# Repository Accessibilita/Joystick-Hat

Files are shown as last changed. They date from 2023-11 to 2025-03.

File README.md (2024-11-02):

# Joystick-HID (0.2a)
A custom open source PCB for controlling an open source wheel chair! This PCB contains all the necessary electronics for interfacing and powering all the components/peripherals that will be used to build a wheel chair human machine interface consisting of this PCB, analog JoyStick module, buttons, rotary switches, and 3D printed housing. JoyStick-HID is just one of the many PCBs being developed for our open source wheel chair electrical system we are developing with the Accessibilita project for the Mobility Independence Foundation (themif.org) !!

Functional Block Diagram of Board 

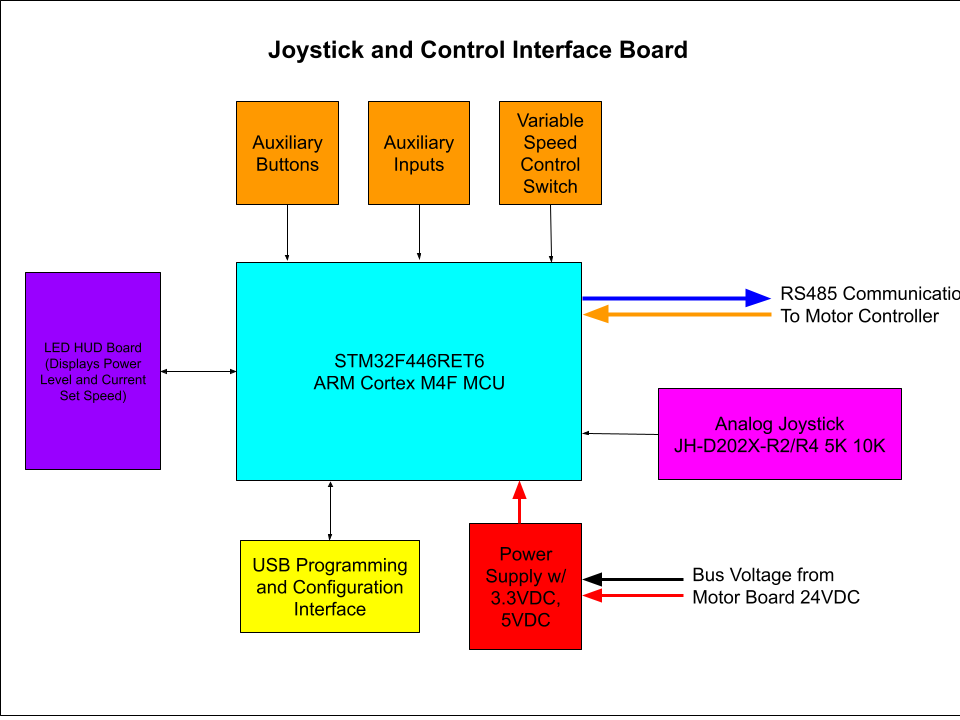
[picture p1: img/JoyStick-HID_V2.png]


Quick Specs of the Hat:
- STM32F446RET6 100TQFP ARM Cortex M4 Microcontoller
- ARM Cortex M Serial Debu Interface/connector for in system programming and development 
- MAX3535ECWI+T RS485 Transceiver for communicating with main motor controller
- D24V22F5 2.5A 5VDC Voltage Regulator Module
- D24V22F3 2.5A 3.3VDC Voltage Regulator Module
- 24V Power Input with High Current Pheonix Contact Connector
- 8 Debug LEDs for STM32F446RET6
- Onboard Battery for STM32F446RET6 RealTime Clock
- Interface for JoyStick, JH-D202X-R2/R4 Joystick 5K https://protosupplies.com/product/jh-d202x-r2-r4-joystick-5k/
- Interface for two Rotary Switches
- Interface for 8 Momentary swiches/buttons
- Interface for LED driver board, this additional board drives LEDs in the arm wrest indicating battery level and current set speed
- STM32 will run FreeRTOS w/ Custom Processes written for all functionality with priority scheduling for safety rated functions.

This hat is intended as a developmental platform that can function in the field, it has all the features needed to control the wheel chair with additional feature that will make software development easier. The final version will be much simpler and low cost, this is only the beginning. 

2D Render of JoyStick-HID Hat in KiCAD 8.0
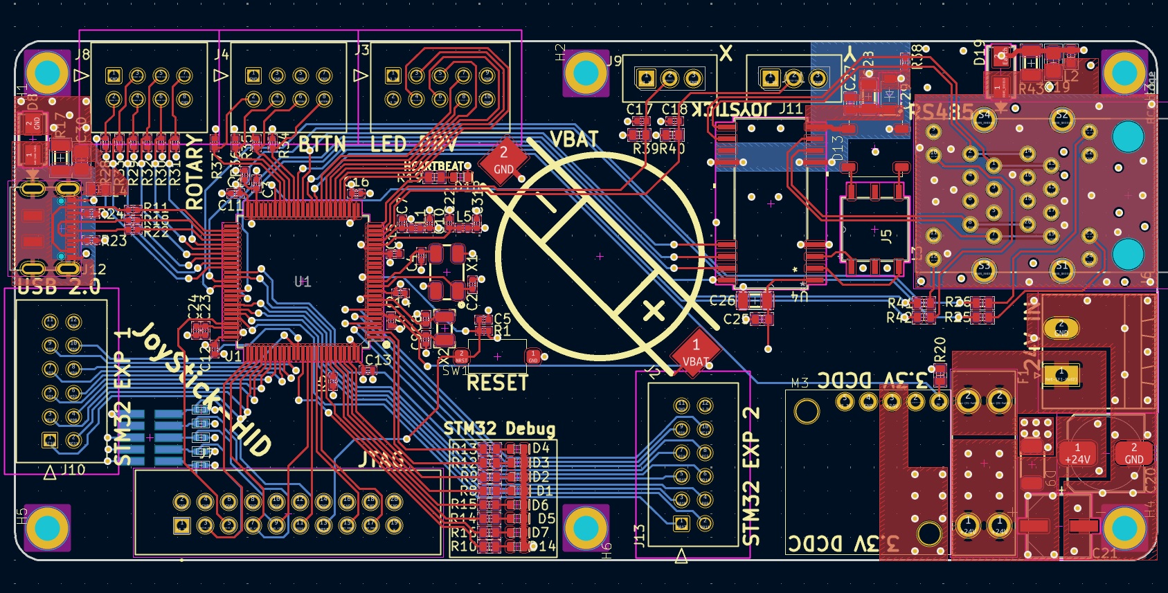
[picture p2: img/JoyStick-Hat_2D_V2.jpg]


3D Renders of JoyStick-HID Hat in KiCAD 8.0 3D Viewer 

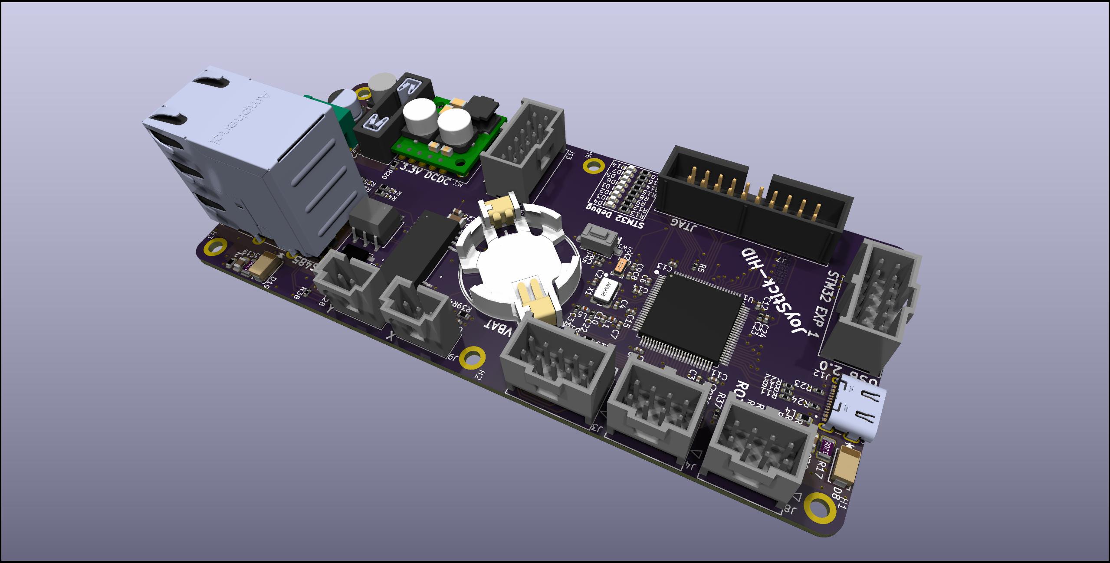
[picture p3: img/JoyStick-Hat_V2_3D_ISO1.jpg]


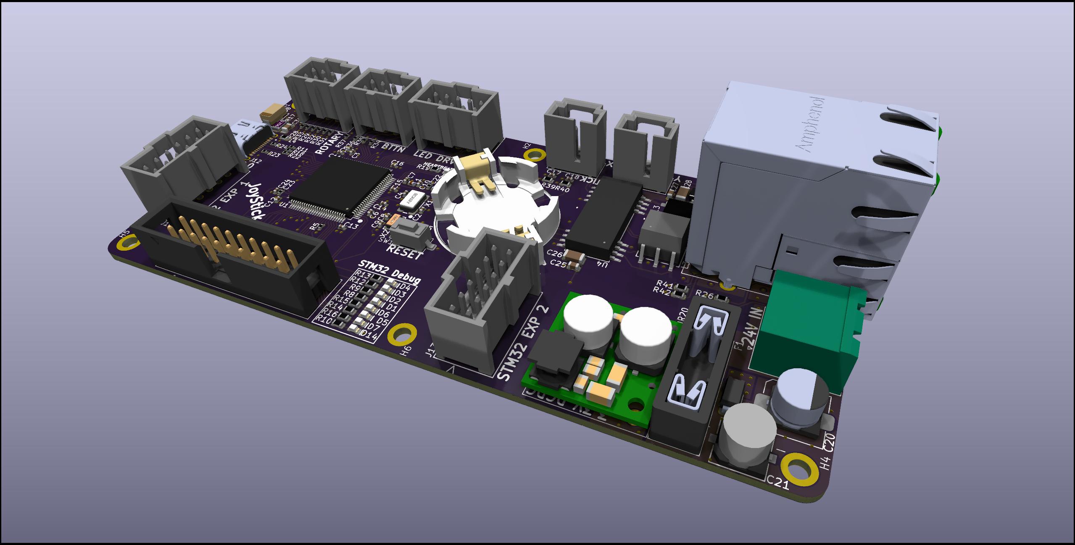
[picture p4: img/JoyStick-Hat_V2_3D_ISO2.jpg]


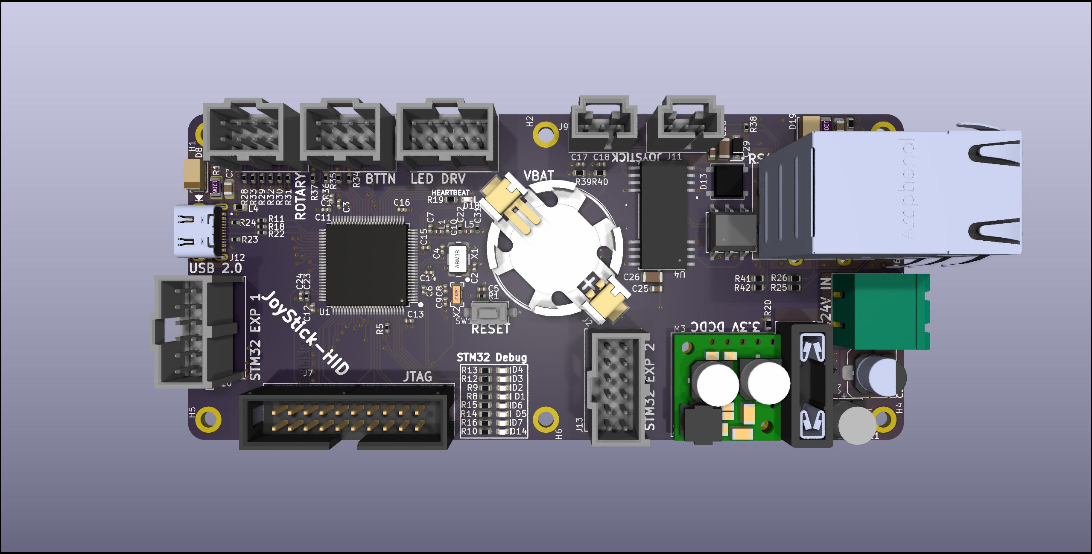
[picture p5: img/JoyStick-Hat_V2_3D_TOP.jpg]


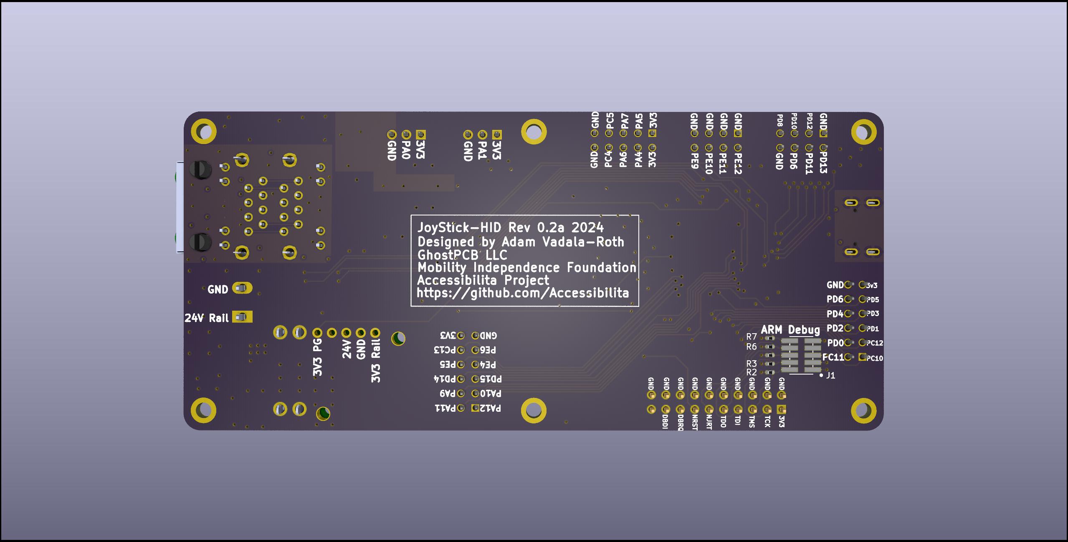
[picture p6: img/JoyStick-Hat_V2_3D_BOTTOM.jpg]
3D_Render_Bottom


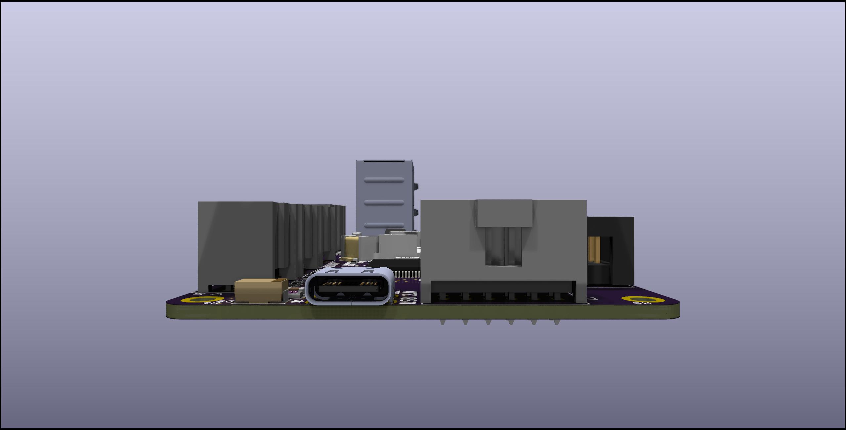
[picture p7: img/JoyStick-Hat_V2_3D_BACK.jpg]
3D_Render_Back


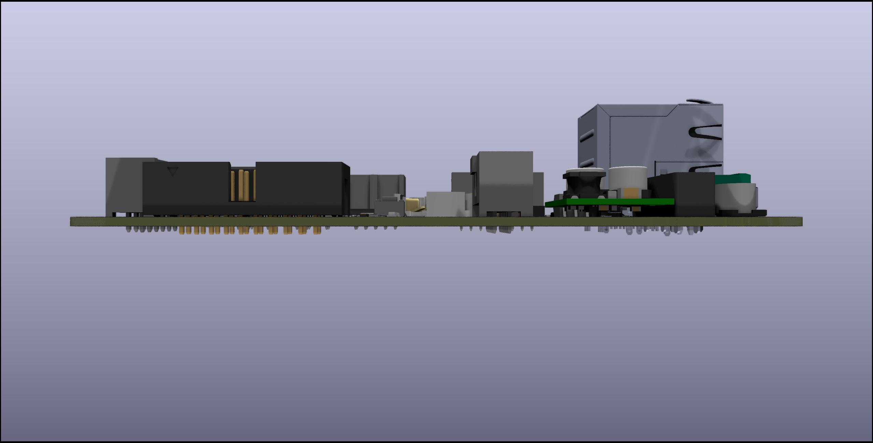
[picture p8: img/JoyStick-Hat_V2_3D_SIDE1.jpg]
3D_Render_SIDE1


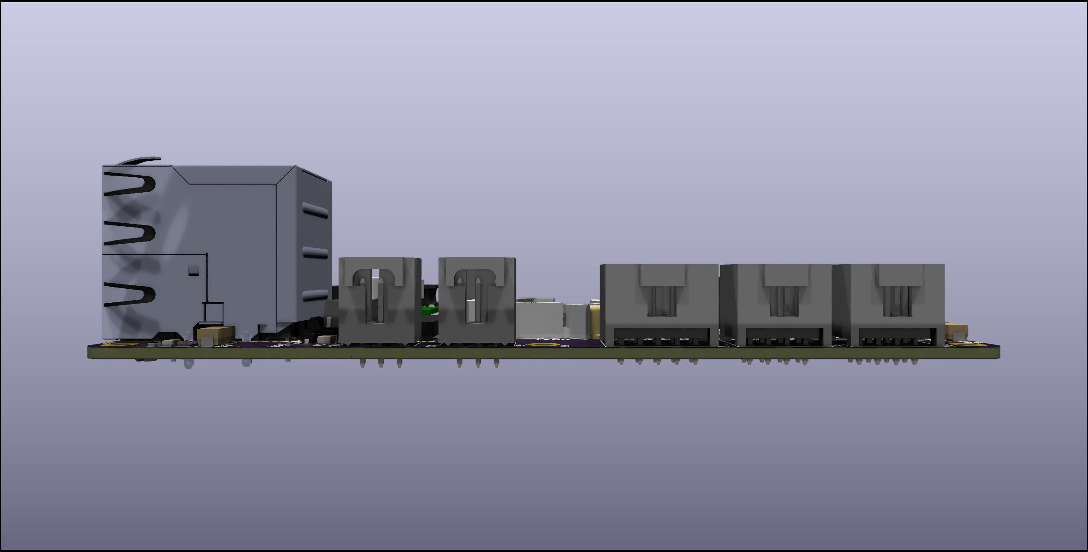
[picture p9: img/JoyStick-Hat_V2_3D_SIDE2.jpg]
3D_Render_SIDE2


# Joystick-Hat (0.1a)
Version 0.1a JoyStick HID:

RPi Hat for controlling an open source wheel chair! This hat contains all the necessary electronics for interfacing and powering all the components/peripherals that will be used to control the open source wheel chair electrical system we are developing with the Accessibilita project !!

Functional Block Diagram of Board 

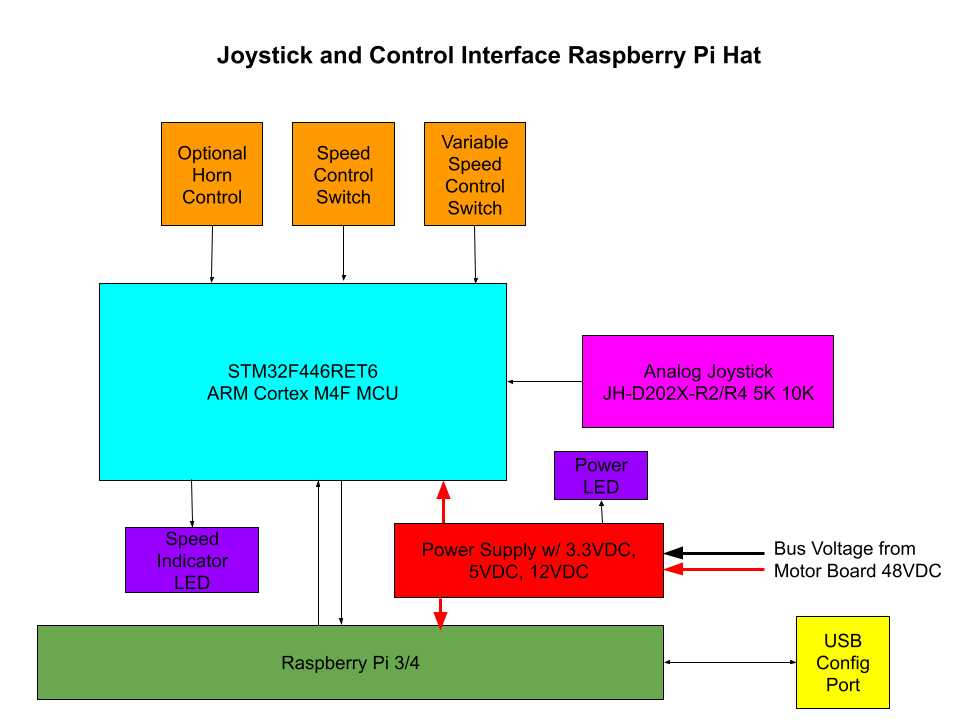
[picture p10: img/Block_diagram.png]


Quick Specs of the Hat:
- STM32F446RET6 100TQFP ARM Cortex M4 Microcontoller
- ARM Cortex M Serial Debu Interface/connector for in system programming and development 
- MAX3535ECWI+T RS485 Transceiver for communicating with main motor controller
- D24V22F5 2.5A 5VDC Voltage Regulator Module
- D24V22F3 2.5A 3.3VDC Voltage Regulator Module
- D24V22F12 2.5A 12VDC Voltage Regulator Module
- 24V Power Input with High Current Pheonix Contact Connector
- 12V Power output with High current Phoenix Contact Connector
- Rapsberry Pi 5 Running ROS2, directly power via header from 5VDC rail
- 8 Debug LEDs for STM32F446RET6
- 8 Debug LEDs for RPi 5
- Onboard Battery for STM32F446RET6 RealTime Clock
- Interface for JoyStick, JH-D202X-R2/R4 Joystick 5K https://protosupplies.com/product/jh-d202x-r2-r4-joystick-5k/
- Interface for two Rotary Switches
- Interface for 8 Momentary swiches/buttons
- Interface for LED driver board, this additional board drives LEDs in the arm wrest indicating battery level and current set speed
- STM32 will run custom FreeRTOS or ROS-Micro more to follow

This hat is intended as a developmental platform that can function in the field, it has all the features needed to control the wheel chair with additional feature that will make software development easier. The final version will be much simpler and low cost, this is only the beginning. 

2D Render of JoyStick-HID Hat in KiCAD 8.0
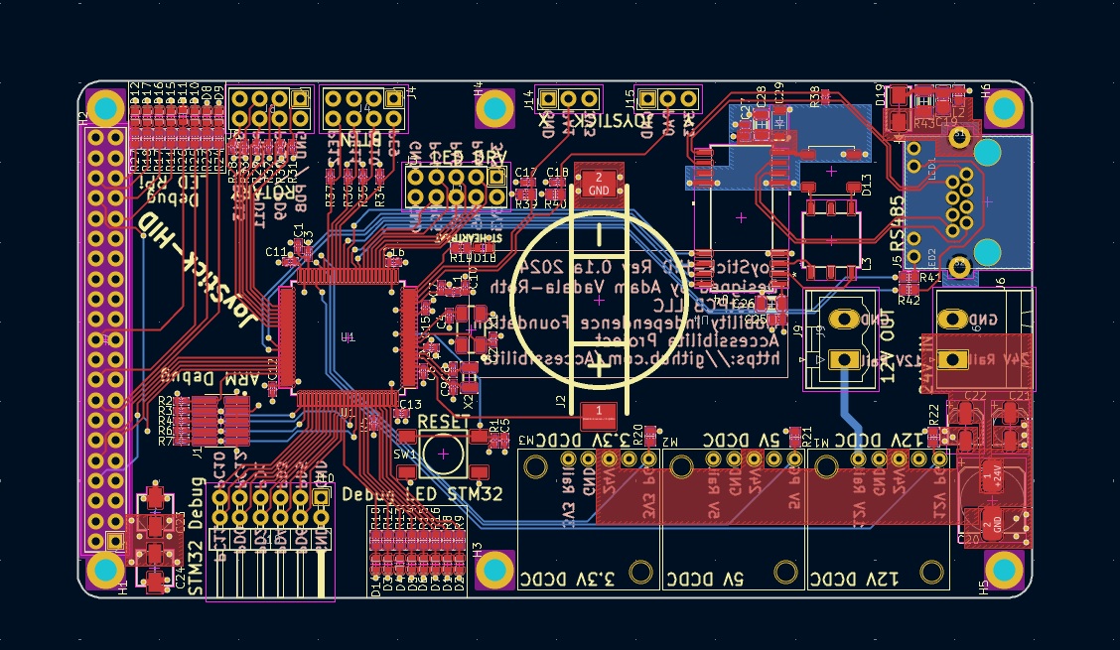
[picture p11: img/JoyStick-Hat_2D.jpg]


3D Renders of JoyStick-HID Hat in KiCAD 8.0 3D Viewer 

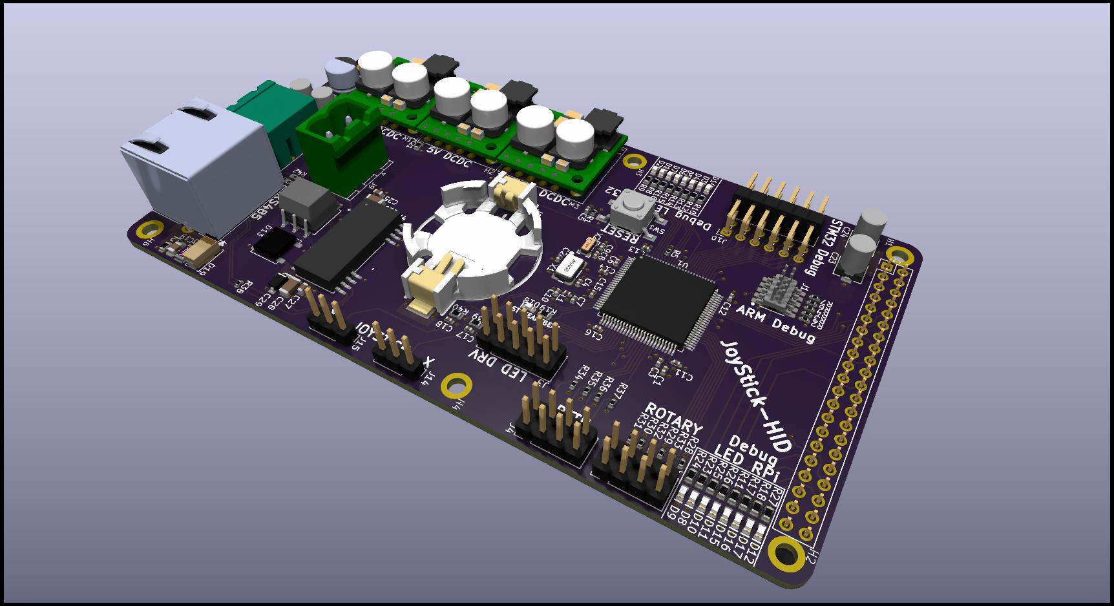
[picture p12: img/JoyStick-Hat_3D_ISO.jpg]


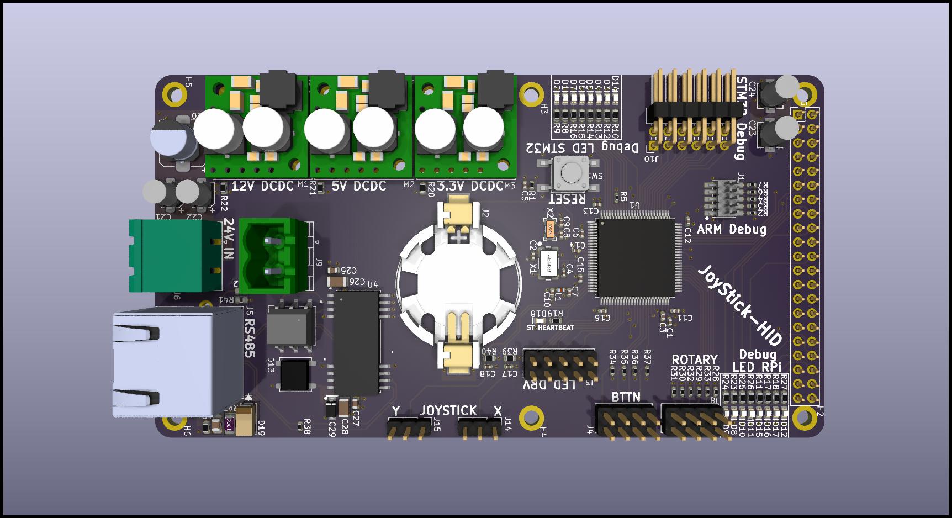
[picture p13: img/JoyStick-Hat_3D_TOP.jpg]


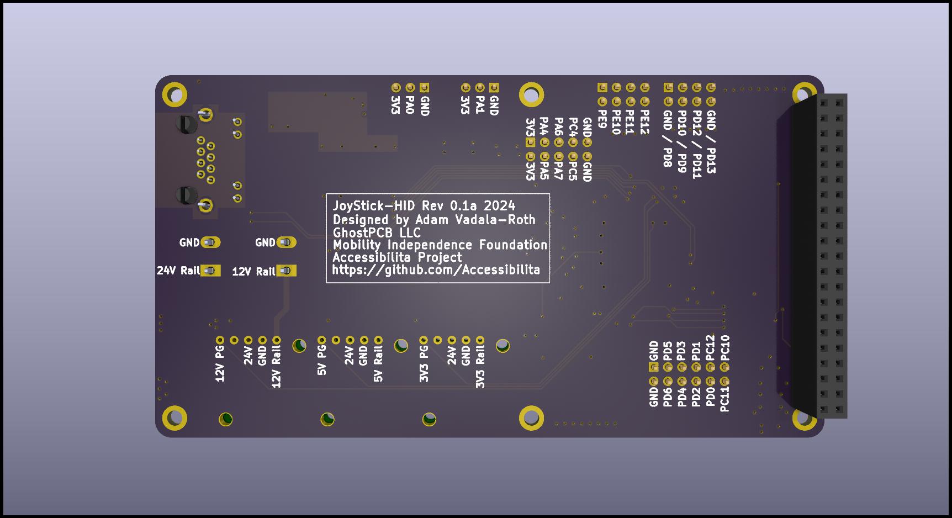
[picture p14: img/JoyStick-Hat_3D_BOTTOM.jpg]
3D_Render_Bottom


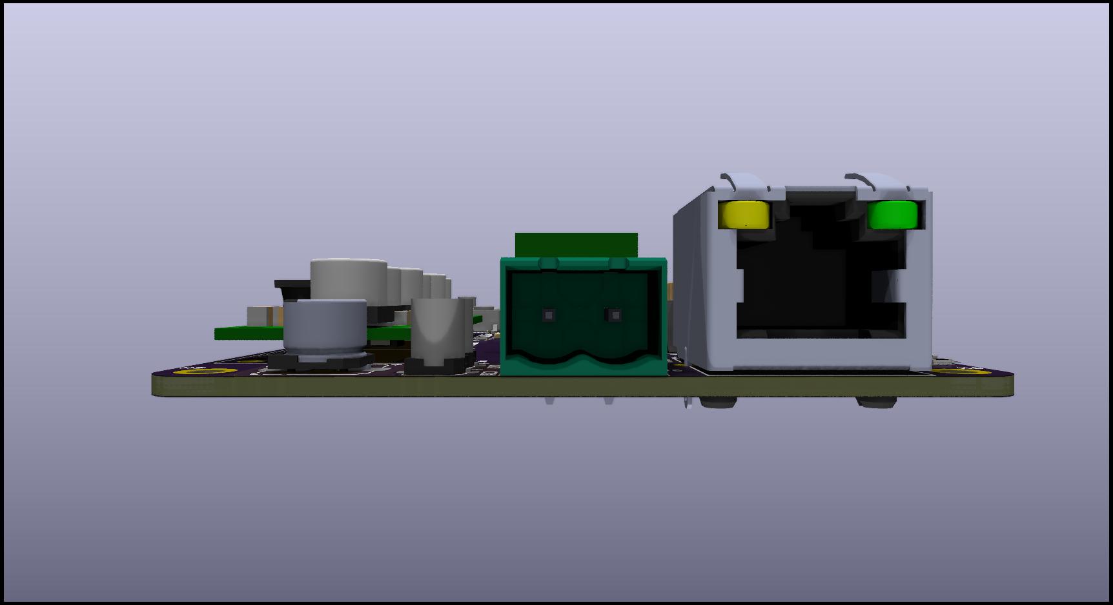
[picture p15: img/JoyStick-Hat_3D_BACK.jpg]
3D_Render_Back


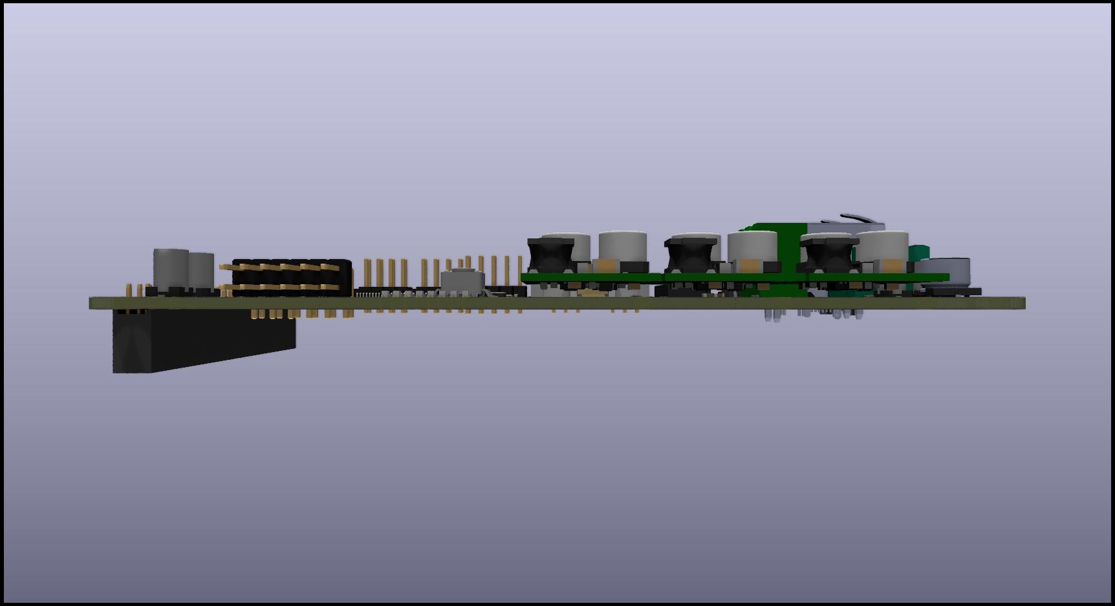
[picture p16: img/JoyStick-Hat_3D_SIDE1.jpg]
3D_Render_SIDE1


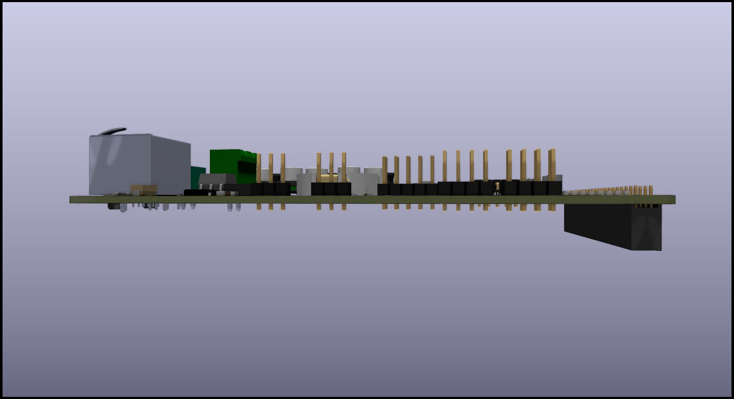
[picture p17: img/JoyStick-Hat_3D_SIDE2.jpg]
3D_Render_SIDE2


# Joystick-Hat (0.1a) Prototype Assembly and Test:

Notes:
assmbely notes:
- Footprint for Raspberry Pi Header connector is wrong, its 42 pins should be 40
- 10uF caps on input = footprint too small!
- C19 footprint too big
- Max chip Pin 1 legend too hard to see
- RS485 diode orientation legend not on PCB
- STM32 Pin 1 legend not there
- Header holes for DCDC regulator modules too small had to hack them on there.
- ARM Cortex M Debug Connector issues, signals are flipped around, the footprint numbering doesn't correspond to the symbol numbering.
- All DCDC Regulators Work and produce correct voltage
- Debug LEDs Work
- GPIO and ADC Interfaces Work

Firmware:
Test firmware along with instructions on how to build and run can be found here: https://github.com/Accessibilita/JoyStick-hat-firmware

## Photos 

Version 0.1a of PCB 90% of Assembled and ready for programming test
Assemnly Progress

Fix for the flpped programming interface from the symbol/footprint number error
Assemnly Progress Fix

Board Hooked Up to Programming Interface with soldered on fix 
Assemnly Progress Fix

Board Powered Up Running Code
Assemnly Progress Fix

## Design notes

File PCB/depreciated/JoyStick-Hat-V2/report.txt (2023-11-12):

Info: Processing symbol 'C1:growbox-KiCAD-Capacitors:C0402'.
Info: Processing symbol 'R25:AVR-KiCAD-Lib-Resistors:R0402'.
Info: Processing symbol 'C2:AVR-KiCAD-Lib-Resistors:R0402'.
Info: Processing symbol 'C3:growbox-KiCAD-Capacitors:C0402'.
Info: Processing symbol 'R26:AVR-KiCAD-Lib-Resistors:R0402'.
Info: Processing symbol 'C4:AVR-KiCAD-Lib-Resistors:R0402'.
Info: Processing symbol 'C5:AVR-KiCAD-Lib-Resistors:R0402'.
Info: Processing symbol 'C6:AVR-KiCAD-Lib-Resistors:R0402'.
Info: Processing symbol 'C7:AVR-KiCAD-Lib-Resistors:R0402'.
Info: Processing symbol 'C8:AVR-KiCAD-Lib-Resistors:R0402'.
Info: Processing symbol 'C9:AVR-KiCAD-Lib-Resistors:R0402'.
Info: Processing symbol 'C10:AVR-KiCAD-Lib-Resistors:R0402'.
Info: Processing symbol 'C11:growbox-KiCAD-Capacitors:C0402'.
Info: Processing symbol 'SW1:AVR-KiCAD-Lib-Mech-Switches:TL3301NF260QG'.
Info: Processing symbol 'C12:growbox-KiCAD-Capacitors:C0402'.
Info: Processing symbol 'U2:AVR-KiCAD-Lib-ICs:DAP32_4P36X4P11'.
Info: Processing symbol 'C13:AVR-KiCAD-Lib-Resistors:R0402'.
Info: Processing symbol 'C14:growbox-KiCAD-Capacitors:C0402'.
Info: Processing symbol 'U3:AVR-KiCAD-Lib-ICs:DAP32_4P36X4P11'.
Info: Processing symbol 'C15:AVR-KiCAD-Lib-Capacitors:C0603'.
Info: Processing symbol 'C16:AVR-KiCAD-Lib-Capacitors:C0603'.
Info: Processing symbol 'C17:AVR-KiCAD-Lib-Capacitors:C0603'.
Info: Processing symbol 'C18:AVR-KiCAD-Lib-Capacitors:C1206'.
Info: Processing symbol 'C19:AVR-KiCAD-Lib-Resistors:R0402'.
Info: Processing symbol 'C20:AVR-KiCAD-Lib-Resistors:R0402'.
Info: Processing symbol 'C21:AVR-KiCAD-Lib-Capacitors:C0603'.
Info: Processing symbol 'C22:AVR-KiCAD-Lib-Capacitors:C1206'.
Info: Processing symbol 'C23:AVR-KiCAD-Lib-Diodes:D_SOD-123'.
Info: Processing symbol 'C24:AVR-KiCAD-Lib-Capacitors:UCM1C470MCL1GS'.
Info: Processing symbol 'C25:AVR-KiCAD-Lib-Capacitors:UCM1C470MCL1GS'.
Info: Processing symbol 'C39:AVR-KiCAD-Lib-Capacitors:C0603'.
Info: Processing symbol 'D1:AVR-KiCAD-Lib-ICs:SOT-23-6_Handsoldering'.
Info: Processing symbol 'D2:AVR-KiCAD-Lib-Diodes:LMB110S-TP'.
Info: Processing symbol 'D8:AVR-KiCAD-Lib-Diodes:SMAJ30CA'.
Info: Processing symbol 'J1:Connector_PinHeader_2.54mm:PinHeader_2x10_P2.54mm_Vertical'.
Info: Processing symbol 'J2:Connector_PinHeader_2.54mm:PinHeader_2x10_P2.54mm_Vertical'.
Info: Processing symbol 'J3:'.
Info: Processing symbol 'U4:AVR-KiCAD-Lib-ICs:21-0145_W28M&plus_9_MXM'.
Info: Processing symbol 'J4:'.
Info: Processing symbol 'U5:Package_QFP:LQFP-100_14x14mm_P0.5mm'.
Info: Processing symbol 'J5:'.
Info: Processing symbol 'X1:AVR-KiCAD-Lib-Oscillators:ABM3B8.000MHZB2T'.
Info: Processing symbol 'J6:'.
Info: Processing symbol 'X2:AVR-KiCAD-Lib-Oscillators:ABS07-32.768KHZ-9-T'.
Info: Processing symbol 'J7:'.
Info: Processing symbol 'J8:'.
Info: Processing symbol 'J9:'.
Info: Processing symbol 'J10:'.
Info: Processing symbol 'J11:'.
Info: Processing symbol 'J12:AVR-KiCAD-Lib-Connectors:BU2032SM-JJ-GTR'.
Info: Processing symbol 'J13:AVR-KiCAD-Lib-Connectors:20021121-00010C4LF'.
Info: Processing symbol 'J14:AVR-KiCAD-Lib-Connectors:USB_Mini-B'.
Info: Processing symbol 'L1:AVR-KiCAD-Lib-Inductors:BLM15HG601SN1D'.
Info: Processing symbol 'L2:AVR-KiCAD-Lib-Inductors:MI0603K300R-10'.
Info: Processing symbol 'L3:AVR-KiCAD-Lib-Transformers:SO6_Q4470-CL_C-SIZE_COC'.
Info: Processing symbol 'M1:AVR-KiCAD-Lib-Modules:D24V22F12'.
Info: Processing symbol 'M2:AVR-KiCAD-Lib-Modules:D24V22F12'.
Info: Processing symbol 'M3:AVR-KiCAD-Lib-Modules:D24V22F12'.
Info: Processing symbol 'R1:AVR-KiCAD-Lib-Resistors:R0402'.
Info: Processing symbol 'R2:AVR-KiCAD-Lib-Resistors:R0603'.
Info: Processing symbol 'R3:AVR-KiCAD-Lib-Resistors:R0402'.
Info: Processing symbol 'R4:AVR-KiCAD-Lib-Resistors:R0603'.
Info: Processing symbol 'R5:AVR-KiCAD-Lib-Resistors:R0402'.
Info: Processing symbol 'R6:AVR-KiCAD-Lib-Resistors:R0603'.
Info: Processing symbol 'R7:AVR-KiCAD-Lib-Resistors:R0402'.
Info: Processing symbol 'R8:AVR-KiCAD-Lib-Resistors:R0402'.
Info: Processing symbol 'R9:AVR-KiCAD-Lib-Resistors:R0402'.
Info: Processing symbol 'R10:AVR-KiCAD-Lib-Resistors:R0603'.
Info: Processing symbol 'R11:AVR-KiCAD-Lib-Resistors:R0603'.
Info: Processing symbol 'R12:AVR-KiCAD-Lib-Resistors:R0603'.
Info: Processing symbol 'R13:AVR-KiCAD-Lib-Resistors:R0402'.
Info: Processing symbol 'R23:AVR-KiCAD-Lib-Resistors:R1206'.
Info: Processing symbol 'R24:AVR-KiCAD-Lib-Resistors:R0402'.
Error: Cannot add C1 (footprint 'growbox-KiCAD-Capacitors:C0402' not found).
Error: Cannot add C3 (footprint 'growbox-KiCAD-Capacitors:C0402' not found).
Error: Cannot add C11 (footprint 'growbox-KiCAD-Capacitors:C0402' not found).
Error: Cannot add C12 (footprint 'growbox-KiCAD-Capacitors:C0402' not found).
Error: Cannot add C14 (footprint 'growbox-KiCAD-Capacitors:C0402' not found).
Error: Cannot add J3 (no footprint assigned).
Error: Cannot add J4 (no footprint assigned).
Error: Cannot add J5 (no footprint assigned).
Error: Cannot add J6 (no footprint assigned).
Error: Cannot add J7 (no footprint assigned).
Error: Cannot add J11 (no footprint assigned).
Error: Cannot add J9 (no footprint assigned).
Error: Cannot add J12 (footprint 'AVR-KiCAD-Lib-Connectors:BU2032SM-JJ-GTR' not found).
Error: Cannot add J8 (no footprint assigned).
Error: Cannot add J10 (no footprint assigned).

Info: Total warnings: 0, errors: 15.

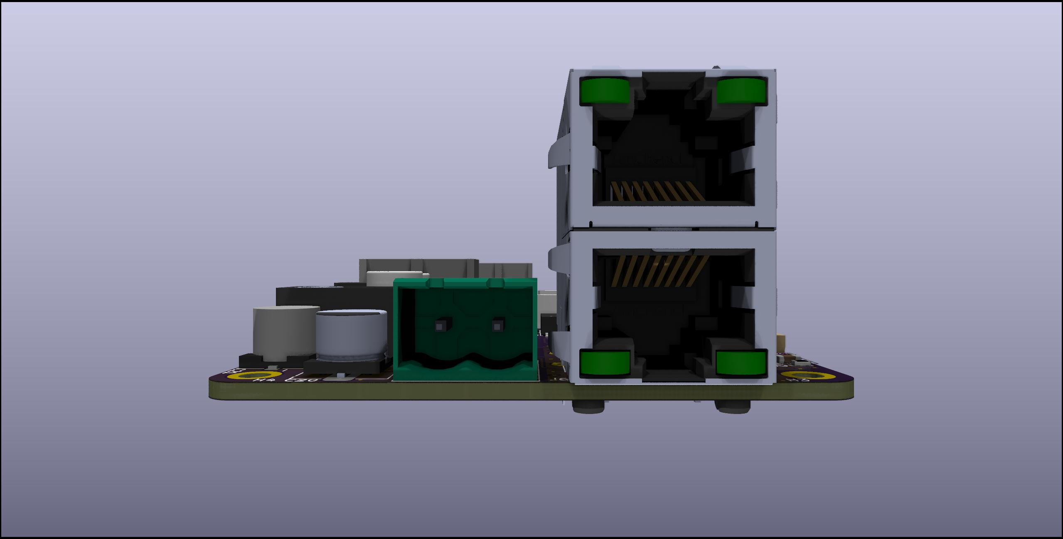
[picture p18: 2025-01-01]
img/JoyStick-Hat_V2_3D_FRONT.jpg

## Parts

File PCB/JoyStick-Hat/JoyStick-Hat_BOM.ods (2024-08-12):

Source: | C:\Users\adamv\OneDrive\Documents\GitHub\Joystick-Hat\PCB\JoyStick-Hat\JoyStick-Hat.kicad_sch
Date: | 1/22/2024 12:37:38 AM
Tool: | Eeschema 7.0.9
Generator: | C:\Program Files\KiCad\7.0\bin\scripting\plugins/bom_csv_grouped_by_value.py
Component Count: | 109
Collated Components:
Item | Qty | Reference(s) | Value | LibPart | Footprint | Datasheet | DNP | Cost QTY: 1 | Cost QTY: 1000 | Cost QTY: 10000 | Cost QTY: 2500 | Cost QTY: 5000 | Date Created | Date Modified | Description | Designer | Height | Lead-Free ? | MFR | MFR# | Management_ID | Mounting | Package | Pin Count # | RoHS Levels | Status | Tolerance | Type | Vendor | Vendor # | Voltage | _Value_
1 | 11 | C1, C5, C6, C7, C10, C11, C12, C13, C14, C15, C16 | C0402C104K9PACTU | AVR-KiCAD-Lib-Capacitors:C0402C104K9PACTU | AVR-KiCAD-Lib-Resistors:R0402 | https://content.kemet.com/datasheets/KEM_C1006_X5R_SMD.pdf |  | 0.1 | 0.01139 | 0.00756 | 0.01035 | 0.00952 | 12/7/2019 | 12/7/2019 | 0.1µF ±10% 6.3V Ceramic Capacitor X5R 0402 (1005 Metric) | AVR | 0.55mm | Yes | KEMET | C0402C104K9PACTU | * | SMT | 402 | 2 | 1 | Active | 10% | Ceramic Cap | Digikey | 399-3026-6-ND | 6.3V | 0.1uF
2 | 2 | C2, C4 | GCM1555C1H180GA16D | AVR-KiCAD-Lib-Capacitors:GCM1555C1H180GA16D | AVR-KiCAD-Lib-Capacitors:C0402 | https://search.murata.co.jp/Ceramy/image/img/A01X/G101/ENG/GCM1555C1H180GA16-01.pdf |  | 0.11 | 0.02079 | 0.01432 | 0.01934 | 0.0177 | 6/16/2020 | 6/16/2020 | 18pF ±2% 50V Ceramic Capacitor C0G, NP0 0402 (1005 Metric) | AVR | 0.55mm | Yes | Murata Electronics | GCM1555C1H180GA16D | * | SMT | 402 | 2 | 1 | Active | 2% | Ceramic CAP | Digikey | 490-16456-2-ND | 50V | 18pF
3 | 1 | C3 | GRM155R60J475ME47D | AVR-KiCAD-Lib-Capacitors:GRM155R60J475ME47D | AVR-KiCAD-Lib-Capacitors:C0402 | https://www.murata.com/~/media/webrenewal/support/library/catalog/products/capacitor/mlcc/c02e.ashx?la=en-us |  | 0.16 | 0.03164 | 0.0198 | 0.02944 | 0.02694 | 6/16/2020 | 6/16/2020 | 4.7µF ±20% 6.3V Ceramic Capacitor X5R 0402 (1005 Metric) | AVR | 0.6mm | Yes | Murata Electronics | GRM155R60J475ME47D | * | SMT | 402 | 2 | 1 | Active | 20% | Ceramic Cap | Digikey | 490-5915-2-ND | 6.3V | 4.7uF
4 | 2 | C8, C9 | CL05C090CB5NNNC | AVR-KiCAD-Lib-Capacitors:CL05C090CB5NNNC | AVR-KiCAD-Lib-Capacitors:C0402 | http://www.samsungsem.com/kr/support/product-search/mlcc/CL05C090CB5NNNC.jsp |  | 0.1 | 0.01352 | 0.00899 | 0.01229 | 0.01131 | 6/16/2020 | 6/16/2020 | 9pF ±0.25pF 50V Ceramic Capacitor C0G, NP0 0402 (1005 Metric) | AVR | 0.55mm | Yers | Samsung Electro-Mechanics | CL05C090CB5NNNC | * | SMT | 402 | 2 | 1 | Active | ±0.25pF | Ceramic Cap | Digikey | 1276-1616-2-ND | 50V | 9pF
5 | 1 | C20 | UUQ1H470MCL1GS | AVR-KiCAD-Lib-Capacitors:UUQ1H470MCL1GS | AVR-KiCAD-Lib-Capacitors:CP_Elec_8x10 | https://www.nichicon.co.jp/english/products/pdfs/e-uuq.pdf |  | 1.06 | * | * | * | * | 12/16/2019 | 12/16/2019 | 47µF 50V Aluminum Electrolytic Capacitors Radial, Can - SMD 1000 Hrs @ 105°C | AVR | 6.2mm | Yes | Nichicon | UUQ1H470MCL1GS | * | SMT | Radial SMD | 2 | 1 | Active | 20% | Alu Cap Audio | Digikey | 493-3212-1-ND | 50V | 47uF
6 | 1 | C21 | UUQ1H100MCL1GB | AVR-KiCAD-Lib-Capacitors:UUQ1H100MCL1GB | AVR-KiCAD-Lib-Capacitors:CP_Elec_4x5.3 | https://www.nichicon.co.jp/english/products/pdfs/e-uuq.pdf |  | 0.72 | 0.24828 | * | * | * | 12/16/2019 | 12/16/2019 | 10µF 50V Aluminum Electrolytic Capacitors Radial, Can - SMD 1000 Hrs @ 105°C | AVR | 5.4mm | Yes | Nichicon | UUQ1H100MCL1GB | * | SMT | Radial SMD | 2 | 1 | Active | 20% | Alu Cap Audio | Digikey | 493-3208-1-ND | 50V | 10uF
7 | 1 | C22 | UUQ1H010MCL1GB | AVR-KiCAD-Lib-Capacitors:UUQ1H010MCL1GB | AVR-KiCAD-Lib-Capacitors:CP_Elec_4x5.3 | https://www.nichicon.co.jp/english/products/pdfs/e-uuq.pdf |  | 0.47 | 0.326 | * | * | * | 12/16/2019 | 12/16/2019 | 1µF 50V Aluminum Electrolytic Capacitors Radial, Can - SMD 1000 Hrs @ 105°C | AVR | 5.4mm | Yes | Nichicon | UUQ1H010MCL1GB | * | SMT | Radial SMD | 2 | 1 | Active | 20% | Alu Cap Audio | Digikey | 493-3207-1-ND | 50V | 1uF
8 | 2 | C23, C24 | UCM1C470MCL1GS | AVR-KiCAD-Lib-Capacitors:UCM1C470MCL1GS | AVR-KiCAD-Lib-Capacitors:UCM1C470MCL1GS | http://nichicon-us.com/english/products/pdfs/e-ucm.pdf |  | 0.6 | 0.17512 | 0.12589 | * | * | 6/21/2020 | 6/21/2020 | 47µF 16V Aluminum Electrolytic Capacitors Radial, Can - SMD 2000 Hrs @ 105°C | AVR | 6.10mm | Yes | Nichicon | UCM1C470MCL1GS | * | SMT | Radial Can SMD | 2 | 1 | Active | 20% | Capacitor | Digikey | 493-14529-2-ND | 16V | 47uF
9 | 2 | C25, C27 | CL10B104JB8NNNC | AVR-KiCAD-Lib-Capacitors:CL10B104JB8NNNC | AVR-KiCAD-Lib-Capacitors:C0603 | https://mm.digikey.com/Volume0/opasdata/d220001/medias/docus/609/CL10B104JB8NNNC_Spec.pdf |  | 0.1 | 0.00975 | * | * | * | 10/3/2023 | 10/3/2023 | 0.1 µF ±5% 50V Ceramic Capacitor X7R 0603 (1608 Metric) | Adam Vadala-Roth | 0.9 | Yes | Samsung Electro-Mechanics | CL10B104JB8NNNC | * | SMT | 603 | 2 | 1 | Active | 5% | Capacitor | Digikey | 1276-1033-2-ND | 50V | 0.1uF
10 | 2 | C26, C28 | CGA5L3X5R1V106K160AB | AVR-KiCAD-Lib-Capacitors:CGA5L3X5R1V106K160AB | AVR-KiCAD-Lib-Capacitors:C1206 | https://product.tdk.com/system/files/dam/doc/product/capacitor/ceramic/mlcc/catalog/mlcc_automotive_general_en.pdf |  | * | * | * | * | * | 10/13/2022 | 10/13/2022 | 10 µF ±10% 35V Ceramic Capacitor X5R 1206 (3216 Metric) | AVR | 1.9mm | Yes | TDK Corporation | CGA5L3X5R1V106K160AB | * | SMT | 1206 | 2 | 1 | Active | 10% | Ceramic Cap | Digikey | 445-7887-2-ND | 35V | 10uF
11 | 1 | C29 | C1206C105K3RACAUTO | AVR-KiCAD-Lib-Capacitors:C1206C105K3RACAUTO | AVR-KiCAD-Lib-Diodes:D_SOD-123 | https://content.kemet.com/datasheets/KEM_C1023_X7R_AUTO_SMD.pdf |  | 0.25 | 0.06064 | 0.04594 | * | * | 7/31/2020 | 7/31/2020 | 1µF ±10% 25V Ceramic Capacitor X7R 1206 (3216 Metric) | AVR | 1.40mm | YES | KEMET | C1206C105K3RACAUTO | * | SMT | 1206 | 2 | 1 | Active | 10% | Capacitor | Digikey | 399-7010-1-ND | 25V | 1uF
12 | 9 | D1, D2, D3, D4, D5, D6, D7, D14, D18 | LTST-C194TBKT | AVR-KiCAD-Lib-Diodes:LTST-C194TBKT | AVR-KiCAD-Lib-Diodes:LED0603 | http://optoelectronics.liteon.com/upload/download/DS22-2010-0025/LTST-C194TBKT.PDF |  | 0.42 | 0.07797 | 0.05424 | * | 0.06102 | 3/1/2020 | 3/1/2020 | Blue 468nm LED Indication - Discrete 3.3V 0603 (1608 Metric) | AVR | 0.45mm | Yes | Lite-On Inc. | LTST-C194TBKT | * | SMT | 603 | 2 | 1 | Active | * | Blue LED Colorless | Digikey | 160-1837-2-ND | 3.3V | Blue LED
13 | 8 | D8, D9, D10, D11, D12, D15, D16, D17 | LTST-C194KGKT | AVR-KiCAD-Lib-Diodes:LTST-C194KGKT | AVR-KiCAD-Lib-Diodes:LED0603 | https://optoelectronics.liteon.com/upload/download/DS22-2010-0197/LTST-C194KGKT.PDF |  | 0.39 | 0.07027 | 0.05382 | 0.06877 | 0.0598 | 5/31/2020 | 5/31/2020 | Green 572nm LED Indication - Discrete 2.1V 0603 (1608 Metric) | AVR | 0.45mm | Yes | Lite-On Inc. | LTST-C194KGKT | * | SMT | 603 | 2 | 1 | Active | * | LED GREEN CLEAR SMD | Digikey | 160-1834-2-ND | 2.1V | GREEN LED
14 | 1 | D13 | LMB110S-TP | AVR-KiCAD-Lib-Diodes:LMB110S-TP | AVR-KiCAD-Lib-Diodes:LMB110S-TP | https://www.mccsemi.com/pdf/Products/LMB12S-LMB110S(LMBS-1).pdf |  | $0.47000 | $0.13736 | $0.10908 | $0.12645 | $0.12120 | 11/11/2023 | 11/11/2023 | Bridge Rectifier Single Phase Schottky 100 V Surface Mount LMBS-1 | Adam Vadala-Roth | 1.5 | Yes | Micro Commercial Co | LMB110S-TP | * | SMT | 4-SMD, Gull Wing | 4 | 1 | Active | * | Diode | Digikey | 353-LMB110S-TPTR-ND | 850 mV @ 500 mA | LMB110S-TP
15 | 6 | H1, H2, H3, H4, H5, H6 | MountingHole_Pad | Mechanical:MountingHole_Pad | AVR-KiCAD-Lib-Holes_Fasteners:RPI_HAT_HOLE | ~
16 | 1 | J1 | 20021121-00010C4LF | AVR-KiCAD-Lib-Connectors:20021121-00010C4LF | AVR-KiCAD-Lib-Connectors:20021121-00010C4LF | https://cdn.amphenol-icc.com/media/wysiwyg/files/drawing/20021121.pdf |  | 0.87 | * | * | * | * | 6/16/2020 | 6/16/2020 | CONN HEADER SMD 10POS 1.27MM | AVR | 5.5mm | Yes | Amphenol ICC (FCI) | 20021121-00010C4LF | * | SMT | * | 10 | 1 | Active | * | SMT Pin Header | Digikey | 609-3695-1-ND | * | 20021121-00010C4LF
17 | 1 | J2 | BU2032SM-JJ-GTR | AVR-KiCAD-Lib-Battery-Holders:BU2032SM-JJ-GTR | AVR-KiCAD-Lib-Battery-Holders:BU2032SM-JJ-GTR | http://www.memoryprotectiondevices.com/datasheets/BU2032SM-JJ-GTR-datasheet.pdf |  | 0.96 | * | * | * | * | 12/7/2019 | 12/7/2019 | Battery Holder (Open) Coin, 20.0mm 1 Cell SMD (SMT) Tab | AVR | 5.3mm | Yes | MPD (Memory Protection Devices) | BU2032SM-JJ-GTR | * | SMT | Proprietary | 2 | 1 | Active | * | Battery Clip | Digikey | BU2032SM-JJ-GCT-ND | 3.3V | Battery Clip
18 | 1 | J3 | Conn_02x05_Odd_Even | Connector_Generic:Conn_02x05_Odd_Even | Connector_PinHeader_2.54mm:PinHeader_2x05_P2.54mm_Vertical | ~
19 | 2 | J4, J8 | Conn_02x04_Odd_Even | Connector_Generic:Conn_02x04_Odd_Even | Connector_PinHeader_2.54mm:PinHeader_2x04_P2.54mm_Vertical | ~
20 | 1 | J5 | 8P8C_LED_Shielded | Connector:8P8C_LED_Shielded | AVR-KiCAD-Lib-Connectors:RJ45_Wuerth_7499111446_Horizontal | ~
21 | 1 | J6 | 1757242 | AVR-KiCAD-Lib-Connectors:1757242 | AVR-KiCAD-Lib-Connectors:PhoenixContact_MSTBA-G_02x5.08mm_Angled | https://media.digikey.com/pdf/Data%20Sheets/Phoenix%20Contact%20PDFs/1757242.pdf |  | 0.64 | 0.45518 | * | 0.43375 | 0.40698 | 6/20/2020 | 6/20/2020 | 2 Position Terminal Block Header, Male Pins, Shrouded (4 Side) 0.200" (5.08mm) 90°, Right Angle Through Hole | AVR | 12mm | Yes | Phoenix Contact | 1757242 | * | ThroughHole | * | 2 | 1 | Active | * | Connector | Digikey | 277-1106-ND | 300V | 1757242
22 | 1 | J7 | Raspberry_Pi_2_3 | Connector:Raspberry_Pi_2_3 | AVR-KiCAD-Lib-Connectors:PinHeader_2x21_P2.54mm_Vertical | https://www.raspberrypi.org/documentation/hardware/raspberrypi/schematics/rpi_SCH_3bplus_1p0_reduced.pdf
23 | 1 | J9 | 1755736 | AVR-KiCAD-Lib-Connectors:1755736 | AVR-KiCAD-Lib-Connectors:PhoenixContact_MSTBVA-G_02x5.08mm_Vertical | https://media.digikey.com/pdf/Data%20Sheets/Phoenix%20Contact%20PDFs/1755794.pdf |  | 0.64 | 0.45518 | * | 0.43375 | 0.40698 | 3/11/2020 | 3/11/2020 | 2 Position Terminal Block Header, Male Pins, Shrouded (4 Side) 0.200" (5.08mm) Vertical Through Hole | AVR | 12mm | Yes | Phoenix Contact | 1755736 | * | ThroughHole | * | 2 | 1 | Active | * | Connector, Terminal Block | Digikey | 277-1150-ND | 300V | 1755736
24 | 1 | J10 | Conn_02x06_Odd_Even | Connector_Generic:Conn_02x06_Odd_Even | Connector_PinHeader_2.54mm:PinHeader_2x06_P2.54mm_Horizontal | ~
25 | 2 | J14, J15 | Conn_01x03_Pin | Connector:Conn_01x03_Pin | Connector_PinHeader_2.54mm:PinHeader_1x03_P2.54mm_Vertical | ~
26 | 1 | L1 | BLM15HG601SN1D | AVR-KiCAD-Lib-Inductors:BLM15HG601SN1D | AVR-KiCAD-Lib-Inductors:BLM15HG601SN1D | https://www.murata.com/en-global/products/productdata/8796740223006/ENFA0024.pdf |  | 0.19 | 0.06013 | 0.0509 | * | 0.05598 | 6/15/2020 | 6/15/2020 | 600 Ohms @ 100MHz 1 Signal Line Ferrite Bead 0402 (1005 Metric) 300mA 700mOhm | AVR | 0.5mm | Yes | Murata Electronics | BLM15HG601SN1D | * | SMT | 402 | 2 | 1 | Active | * | Ferrite Bead | Digikey | 490-3998-2-ND | * | 600 Ohms @ 100MHz
27 | 1 | L3 | Q4470-CL | AVR-KiCAD-Lib-Transformers:Q4470-CL | AVR-KiCAD-Lib-Transformers:SO6_Q4470-CL_C-SIZE_COC | https://www.coilcraft.com/getmedia/97b6ad34-63ed-485c-a3ac-2a258e22c8ff/mintrans.pdf |  | $2.12 | $1.38 | * | * | $1.09 | 11/11/2023 | 11/11/2023 | miniature transformers were developed for use with | Adam Vadala-Roth | 5.46mm | Yes | Coilcraft | Q4470-CL | Maxim RS-232/RS-485 interface ICs | SMT | Proprietary | 6 | 1 | Active | * | Transformer | Coilcraft | Q4470-CL | 5V | Q4470-CL
28 | 1 | M1 | D24V22F12 | AVR-KiCAD-Lib-Modules:D24V22F12 | AVR-KiCAD-Lib-Modules:D24V22F12 | https://www.pololu.com/product/2855 |  | 12.95 | * | * | * | * | 9/26/2023 | 9/26/2023 | DCDC Regulator Module 24-36V IN 12VDC OUT | Adam Vadala-Roth | 6mm | Yes | Pololu Robotics & Electronics | D24V22F12 | * | ThroughHole | Proprietary | 5 | 1 | Active | N/A | Module | Pololu Robotics & Electronics | D24V22F12 | 36V IN 12V OUT | D24V22F12
29 | 1 | M2 | D24V22F5 | AVR-KiCAD-Lib-Modules:D24V22F5 | AVR-KiCAD-Lib-Modules:D24V22F12 | https://www.pololu.com/product/2858 |  | 11.95 | * | * | * | * | 9/26/2023 | 9/26/2023 | DCDC Regulator Module 24-36V IN 5VDC OUT | Adam Vadala-Roth | 6mm | Yes | Pololu Robotics & Electronics | D24V22F5 | * | ThroughHole | Proprietary | 5 | 1 | Active | N/A | Module | Pololu Robotics & Electronics | D24V22F5 | 36V IN 5V OUT | D24V22F5
30 | 1 | M3 | D24V22F3 | AVR-KiCAD-Lib-Modules:D24V22F3 | AVR-KiCAD-Lib-Modules:D24V22F12 | https://www.pololu.com/product/2857 |  | 11.95 | * | * | * | * | 9/26/2023 | 9/26/2023 | DCDC Regulator Module 24-36V IN 3.3VDC OUT | Adam Vadala-Roth | 6mm | Yes | Pololu Robotics & Electronics | D24V22F3 | * | ThroughHole | Proprietary | 5 | 1 | Active | N/A | Module | Pololu Robotics & Electronics | D24V22F5 | 36V IN 3.3V OUT | D24V22F3
31 | 16 | R1, R2, R3, R4, R6, R7, R28, R29, R30, R31, R32, R33, R34, R35, R36, R37 | RC0402FR-071KL | AVR-KiCAD-Lib-Resistors:RC0402FR-071KL | AVR-KiCAD-Lib-Resistors:R0402 | https://www.yageo.com/upload/media/product/productsearch/datasheet/rchip/PYu-RC_Group_51_RoHS_L_10.pdf |  | 0.1 | 0.00289 | 0.00163 | 0.00251 | 0.00207 | 12/11/2019 | 12/11/2019 | kOhms ±1% 0.063W, 1/16W Chip Resistor 0402 (1005 Metric) Moisture Resistant Thick Film | AVR | 0.4mm | Yes | Yageo | RC0402FR-071KL | * | SMT | 402 | 2 | 1 | Active | 1% | Thick Film Resistor | Digikey | 311-1.00KLRTR-ND | * | 1K
32 | 1 | R5 | RC0402FR-0710KL | AVR-KiCAD-Lib-Resistors:RC0402FR-0710KL | AVR-KiCAD-Lib-Resistors:R0402 | https://www.yageo.com/upload/media/product/productsearch/datasheet/rchip/PYu-RC_Group_51_RoHS_L_10.pdf |  | 0.1 | 0.00289 | * | 0.00251 | 0.00207 | 12/11/2019 | 12/11/2019 | 10 kOhms ±1% 0.063W, 1/16W Chip Resistor 0402 (1005 Metric) Moisture Resistant Thick Film | AVR | 0.4mm | Yes | Yageo | RC0402FR-0710KL | * | SMT | 402 | 2 | 1 | Active | 1% | Thick FIlm Resistor | Digikey | 311-10.0KLRCT-ND | * | 10K
33 | 17 | R8, R9, R10, R11, R12, R13, R14, R15, R16, R17, R18, R19, R23, R24, R25, R26, R27 | RC0603FR-07470RL | AVR-KiCAD-Lib-Resistors:RC0603FR-07470RL | AVR-KiCAD-Lib-Resistors:R0603 |  |  | 0.1 | 0.00476 | * | 0.00418 | * | 4/23/2019 | 4/23/2019 | RES SMD 470 OHM 1% 1/10W 0603 | AVR | 0.55mm | Yes | Yageo | RC0603FR-07470RL | * | SMT | 603 | 2 | 1 | Active | 1% | SMT Chip Resistor | Digikey | 311-470HRCT-ND | * | 470r
34 | 3 | R20, R21, R22 | RC0603JR-07270RL | AVR-KiCAD-Lib-Resistors:RC0603JR-07270RL | AVR-KiCAD-Lib-Resistors:R0603 | https://www.yageo.com/upload/media/product/productsearch/datasheet/rchip/PYu-RC_Group_51_RoHS_L_12.pdf |  | 0.1 | 0.00415 | 0.00262 | * | 0.00298 | 9/26/2023 | 9/26/2023 | RES 270 OHM 5% 1/10W 0603 | Adam Vadala-Roth | 0.55mm | Yes | YAGEO | RC0603JR-07270RL | * | SMT | 603 | 2 | 1 | Active | 1% | Resistor | Digikey | 311-270GRTR-ND | N/A | 270
35 | 1 | SW1 | TL3301NF260QG | AVR-KiCAD-Lib-Mech-Switches:TL3301NF260QG | AVR-KiCAD-Lib-Mech-Switches:TL3301NF260QG | http://spec_sheets.e-switch.com/specs/P010517.pdf |  | 0.38 | * | * | * | * | 2/28/2020 | 2/28/2020 | Tactile Switch SPST-NO Top Actuated Surface Mount | AVR | 4.4mm | Yes | E-Switch | TL3301NF260QG | * | SMT | Proprietary | 4 | 1 | Active | * | Mechanical Momentary Switch | Digikey | EG1868TR-ND | 12VDC | TL3301NF260QG
36 | 1 | U1 | STM32F446VETx | MCU_ST_STM32F4:STM32F446VETx | Package_QFP:LQFP-100_14x14mm_P0.5mm | https://www.st.com/resource/en/datasheet/stm32f446ve.pdf
37 | 1 | U4 | MAX3535ECWI+T | AVR-KiCAD-Lib-ICs:MAX3535ECWI+T | AVR-KiCAD-Lib-ICs:21-0145_W28M&plus_9_MXM | https://www.analog.com/media/en/technical-documentation/data-sheets/max3535e-mxl1535e.pdf |  | 13.07 | 8.27473 | * | * | * | 10/4/2023 | 10/4/2023 | 1/1 Transceiver Full RS422, RS485 28-SOIC | Adam Vadala-Roth | 2.65mm | Yes | Analog Devices Inc./Maxim Integrated | MAX3535ECWI+T | * | SMT | SOIC28 (16 Leads) | 16 | 1 | Active | N/A | Integrated Circuit | Digikey | MAX3535ECWI+TTR-ND | 3-5.5V | MAX3535ECWI+T
38 | 1 | X1 | ABM3B-8.000MHZ-B2-T | AVR-KiCAD-Lib-Oscillators-Clocks:ABM3B-8.000MHZ-B2-T | AVR-KiCAD-Lib-Oscillators:ABM3B8.000MHZB2T | https://abracon.com/Resonators/abm3b.pdf |  | 1.09 | 0.57 | * | * | * | 6/16/2020 | 6/16/2020 | 8MHz ±20ppm Crystal 18pF 200 Ohms 4-SMD, No Lead | AVR | 1.10mm | Yes | Abracon LLC | ABM3B-8.000MHZ-B2-T | * | SMT | 4-SMD | 4 | 1 | Active | * | Crystal Oscillator | Digikey | 535-9720-2-ND | * | 8MHZ
39 | 1 | X2 | ABS07-32.768KHZ-9-T | AVR-KiCAD-Lib-Oscillators-Clocks:ABS07-32.768KHZ-9-T | AVR-KiCAD-Lib-Oscillators:ABS07-32.768KHZ-9-T | https://abracon.com/Resonators/ABS07.pdf |  | 1.09 | 0.627 | * | * | * | 6/16/2020 | 6/16/2020 | 32.768kHz ±20ppm Crystal 9pF 70 kOhms 2-SMD, No Lead | AVR | 0.9mm | Yes | Abracon LLC | ABS07-32.768KHZ-9-T | * | SMT | Proprietary SMT | 2 | 1 | Active | * | Crystal Oscillator | Digikey | 535-9544-1-ND | * | 32.7680KHZ

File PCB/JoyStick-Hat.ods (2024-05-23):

Reference | Value | Datasheet | Footprint | Qty | DNP
C1,C4,C6 | UFW1H100MDD1TD | http://nichicon-us.com/english/products/pdfs/e-ufw.pdf | AVR-KiCAD-Lib-Capacitors:CP_Radial_D5.0mm_P2.50mm | 3
C2,C3,C8 | UVR2A0R1MDD1TD | http://nichicon-us.com/english/products/pdfs/e-uvr.pdf | AVR-KiCAD-Lib-Capacitors:CP_Radial_D5.0mm_P2.50mm | 3
C5 | CL21C470JC61PNC | https://www.samsungsem.com/kr/support/product-search/mlcc/__icsFiles/afieldfile/2018/06/11/CL21C470JC61PNC.pdf | AVR-KiCAD-Lib-Capacitors:C0805 | 1
C7 | UFW1H101MPD | http://nichicon-us.com/english/products/pdfs/e-ufw.pdf | AVR-KiCAD-Lib-Capacitors:CP_Radial_D8.0mm_P3.50mm | 1
C9 | UUQ1H470MCL1GS | https://www.nichicon.co.jp/english/products/pdfs/e-uuq.pdf | AVR-KiCAD-Lib-Capacitors:CP_Elec_8x10 | 1
D1 | HLMP-4700-C0002 |  | AVR-KiCAD-Lib-Diodes:LED_D5.0mm | 1
D2 | 1N47xxA | https://www.vishay.com/docs/85816/1n4728a.pdf | Diodes_ThroughHole:D_DO-35_SOD27_P10.16mm_Horizontal | 1
FB1,FB2 | FBMJ1608HM180NTR | https://www.yuden.co.jp/productdata/catalog/chipbeads01_e.pdf | AVR-KiCAD-Lib-Resistors:R0603 | 2
Q1 | 2N5457 | https://www.mouser.com/datasheet/2/68/2n5457-5459-1518584.pdf | AVR-KiCAD-Lib-Transistors:TO-92 | 1
Q2 | 2N3904BU | https://www.onsemi.com/pub/Collateral/PZT3904-D.pdf | AVR-KiCAD-Lib-Transistors:TO-92 | 1
Q3 | 2N7000 | https://www.onsemi.com/pub/Collateral/NDS7002A-D.PDF | AVR-KiCAD-Lib-Transistors:TO-92 | 1
R1,R3,R11 | RC1206FR-0710ML | http://www.yageo.com/documents/recent/PYu-RC_Group_51_RoHS_L_10.pdf | AVR-KiCAD-Lib-Resistors:R1206 | 3
R2 | RC1206JR-072M2L | http://www.yageo.com/documents/recent/PYu-RC_Group_51_RoHS_L_10.pdf | AVR-KiCAD-Lib-Resistors:R1206 | 1
R4 | RC1206FR-071ML | http://www.yageo.com/documents/recent/PYu-RC_Group_51_RoHS_L_10.pdf | AVR-KiCAD-Lib-Resistors:R1206 | 1
R5,R6 | RC1206FR-0710KL | http://www.yageo.com/documents/recent/PYu-RC_Group_51_RoHS_L_10.pdf | AVR-KiCAD-Lib-Resistors:R1206 | 2
R7 | RT0603DRD071KL |  | AVR-KiCAD-Lib-Resistors:R0603 | 1
R8 | RC1206FR-071KL |  | AVR-KiCAD-Lib-Resistors:R1206 | 1
R9 | RC1206FR-07100KL | http://www.yageo.com/documents/recent/PYu-RC_Group_51_RoHS_L_10.pdf | AVR-KiCAD-Lib-Resistors:R1206 | 1
R10 | P0915N-EC15BR100K | https://www.ttelectronics.com/TTElectronics/media/ProductFiles/Potentiometers/Datasheets/P09x.pdf | AVR-KiCAD-Lib-Potentiometers:P0915N-FC15BR10K | 1
R12 | RC1206FR-0768KL | http://www.yageo.com/documents/recent/PYu-RC_Group_51_RoHS_L_10.pdf | AVR-KiCAD-Lib-Resistors:R1206 | 1
R13,R14 | RC1206FR-072K7L | http://www.yageo.com/documents/recent/PYu-RC_Group_51_RoHS_L_10.pdf | AVR-KiCAD-Lib-Resistors:R1206 | 2
SP1 | 3PDT-StompSwitch_Alt |  | AVR-KiCAD-Lib-Special:Switches_Stomp_Switch_3PDT | 1
T1,T4 | ACJS-MHDR | https://www.amphenol-sine.com/pdf/datasheet/ACJS-MHDR.pdf | AVR-KiCAD-Lib-Connectors:ACJS-MHDR | 2
T2 | PPPC052LFBN-RC | https://media.digikey.com/pdf/Data%20Sheets/Sullins%20PDFs/Female_Headers.100_DS.pdf | AVR-KiCAD-Lib-Connectors:PPPC052LFBN-RC_2x05_Pitch2.54mm | 1
T3 | PRPC005DAAN-RC | https://drawings-pdf.s3.amazonaws.com/11636.pdf | Pin_Headers:Pin_Header_Straight_2x05_Pitch2.54mm | 1
T5 | 54-00129 |  | AVR-KiCAD-Lib-Connectors:BarrelJack_Horizontal | 1

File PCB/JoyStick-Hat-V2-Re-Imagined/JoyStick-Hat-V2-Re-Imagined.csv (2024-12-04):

Reference | Datasheet | Qty | DNP | Type | Vendor | Vendor # | _Value_ | Description
C1,C5,C6,C7,C10,C11,C12,C13,C14,C15,C16,C17,C18,C22,C23,C31 | https://content.kemet.com/datasheets/KEM_C1006_X5R_SMD.pdf | 16 |  | Ceramic Cap | Digikey | 399-3026-6-ND | 0.1uF | 0.1µF ±10% 6.3V Ceramic Capacitor X5R 0402 (1005 Metric)
C2,C4 | https://search.murata.co.jp/Ceramy/image/img/A01X/G101/ENG/GCM1555C1H180GA16-01.pdf | 2 |  | Ceramic CAP | Digikey | 490-16456-2-ND | 18pF | 18pF ±2% 50V Ceramic Capacitor C0G, NP0 0402 (1005 Metric)
C3,C24 | https://www.murata.com/~/media/webrenewal/support/library/catalog/products/capacitor/mlcc/c02e.ashx?la=en-us | 2 |  | Ceramic Cap | Digikey | 490-5915-2-ND | 4.7uF | 4.7µF ±20% 6.3V Ceramic Capacitor X5R 0402 (1005 Metric)
C8,C9 | http://www.samsungsem.com/kr/support/product-search/mlcc/CL05C090CB5NNNC.jsp | 2 |  | Ceramic Cap | Digikey | 1276-1616-2-ND | 9pF | 9pF ±0.25pF 50V Ceramic Capacitor C0G, NP0 0402 (1005 Metric)
C19,C30 | https://content.kemet.com/datasheets/KEM_C1076_X7R_HV_AUTO_SMD.pdf | 2 |  | SMT Ceramic Cap | Digikey | 399-16644-1-ND | 10nF | CAP CER 0805 10NF 500V X7R 10%
C20 | https://www.nichicon.co.jp/english/products/pdfs/e-uuq.pdf | 1 |  | Alu Cap Audio | Digikey | 493-3212-1-ND | 47uF | 47µF 50V Aluminum Electrolytic Capacitors Radial, Can - SMD 1000 Hrs @ 105°C
C21 | https://www.nichicon.co.jp/english/products/pdfs/e-uuq.pdf | 1 |  | Alu Cap Audio | Digikey | 493-3208-1-ND | 10uF | 10µF 50V Aluminum Electrolytic Capacitors Radial, Can - SMD 1000 Hrs @ 105°C
C25,C27 | https://mm.digikey.com/Volume0/opasdata/d220001/medias/docus/609/CL10B104JB8NNNC_Spec.pdf | 2 |  | Capacitor | Digikey | 1276-1033-2-ND | 0.1uF | 0.1 µF ±5% 50V Ceramic Capacitor X7R 0603 (1608 Metric)
C26,C28 | https://product.tdk.com/system/files/dam/doc/product/capacitor/ceramic/mlcc/catalog/mlcc_automotive_general_en.pdf | 2 |  | Ceramic Cap | Digikey | 445-7887-2-ND | 10uF | 10 µF ±10% 35V Ceramic Capacitor X5R 1206 (3216 Metric)
C29 | https://content.kemet.com/datasheets/KEM_C1023_X7R_AUTO_SMD.pdf | 1 |  | Capacitor | Digikey | 399-7010-1-ND | 1uF | 1µF ±10% 25V Ceramic Capacitor X7R 1206 (3216 Metric)
D1,D2,D3,D4,D5,D6,D7,D14,D18 | http://optoelectronics.liteon.com/upload/download/DS22-2010-0025/LTST-C194TBKT.PDF | 9 |  | Blue LED Colorless | Digikey | 160-1837-2-ND | Blue LED | Blue 468nm LED Indication - Discrete 3.3V 0603 (1608 Metric)
D8,D19 | https://www.littelfuse.com/~/media/electronics/datasheets/tvs_diodes/littelfuse_tvs_diode_smaj_datasheet.pdf.pdf | 2 |  | TVS Diode Zener | Digikey | SMAJ30CALFCT-ND | SMAJ30CA | 48.4V Clamp 8.3A Ipp Tvs Diode Surface Mount DO-214AC (SMA)
D9 | https://www.bourns.com/docs/Product-Datasheets/SMAJ.pdf | 1 |  | Diode | Digikey | SMAJ24ABTR-ND | SMAJ24A | 38.9V Clamp 10.3A Ipp Tvs Diode Surface Mount DO-214AC (SMA)
D13 | https://www.mccsemi.com/pdf/Products/LMB12S-LMB110S(LMBS-1).pdf | 1 |  | Diode | Digikey | 353-LMB110S-TPTR-ND | LMB110S-TP | Bridge Rectifier Single Phase Schottky 100 V Surface Mount LMBS-1
F1 | https://www.keyelco.com/userAssets/file/M65p41.pdf | 1 |  | Fuse Holder | Digikey | 36-3557-2-ND | 3557-2 | Fuse Block 30 A 500V 1 Circuit Blade Through Hole
H1,H2,H3,H4,H5,H6 | ~ | 6
J1 | https://cdn.amphenol-icc.com/media/wysiwyg/files/drawing/20021121.pdf | 1 |  | SMT Pin Header | Digikey | 609-3695-1-ND | 20021121-00010C4LF | CONN HEADER SMD 10POS 1.27MM
J2 | http://www.memoryprotectiondevices.com/datasheets/BU2032SM-JJ-GTR-datasheet.pdf | 1 |  | Battery Clip | Digikey | BU2032SM-JJ-GCT-ND | Battery Clip | Battery Holder (Open) Coin, 20.0mm 1 Cell SMD (SMT) Tab
J3 | https://www.molex.com/content/dam/molex/molex-dot-com/products/automated/en-us/salesdrawingpdf/901/90130/901301210_sd.pdf?inline | 1 |  | Connector | Digikey | WM8249-ND | 0901301210 | Connector Header Through Hole 10 position 0.100" (2.54mm)
J4,J8 | https://www.molex.com/content/dam/molex/molex-dot-com/products/automated/en-us/salesdrawingpdf/901/90130/901301108_sd.pdf?inline | 2 |  | Connector | Digikey | WM8234-ND | 0901301108 | Connector Header Through Hole 8 position 0.100" (2.54mm)
J5 | https://cdn.amphenol-cs.com/media/wysiwyg/files/drawing/rjsaex38x02x.pdf | 1 |  | Connector | Digikey | RJSAE-538A-02-ND | RJSAE-538A-02 | Jack Modular Connector 8p8c (RJ45, Ethernet) 90° Angle (Right) Shielded, EMI Finger
J6 | https://media.digikey.com/pdf/Data%20Sheets/Phoenix%20Contact%20PDFs/1757242.pdf | 1 |  | Connector | Digikey | 277-1106-ND | 1757242 | 2 Position Terminal Block Header, Male Pins, Shrouded (4 Side) 0.200" (5.08mm) 90°, Right Angle Through Hole
J7 | https://s3.amazonaws.com/catalogspreads-pdf/PAGE122%20.100%20SBH11%20SERIES%20MALE%20BOX%20HDR%20ST%20RA%20SMT.pdf | 1 |  | Connector | Digikey | S9172-ND | SBH11-PBPC-D10-ST-BK | Connector Header Through Hole 20 position 0.100" (2.54mm)
J9,J11 | https://www.molex.com/pdm_docs/sd/705430001_sd.pdf | 2 |  | Shrouded Header | Digikey | WM4801-ND | 0705430002 | Connector Header Through Hole 3 position 0.100" (2.54mm)
J10 | https://www.molex.com/content/dam/molex/molex-dot-com/products/automated/en-us/salesdrawingpdf/901/90130/901301210_sd.pdf?inline | 1 |  | Connector | Digikey | WM8250-ND | 0901301212 | Connector Header Through Hole 10 position 0.100" (2.54mm)
J12 | https://www.jae.com/direct/topics/topics_file_download/?topics_id=91780&ext_no=04&_lang=en&v=2020041313384666992409 | 1 |  | USB-C | Digikey | 670-DX07S016JA1R1500TR-ND | DX07S016JA1R1500 | USB-C (USB TYPE-C) USB 2.0 Receptacle Connector 24 (16+8 Dummy) Position Surface Mount, Right Angle; Through Hole
L1,L5 | https://www.murata.com/en-global/products/productdata/8796740223006/ENFA0024.pdf | 2 |  | Ferrite Bead | Digikey | 490-3998-2-ND | 600 Ohms @ 100MHz | 600 Ohms @ 100MHz 1 Signal Line Ferrite Bead 0402 (1005 Metric) 300mA 700mOhm
L2,L4 | https://www.laird.com/sites/default/files/2018-11/Catalog_EMI%20FILTERING%20RF%200717.pdf | 2 |  | Ferrite Bead | Digikey | 240-2373-1-ND | MI0603K300R-10 | 30 Ohms @ 100MHz 1 Power Line Ferrite Bead 0603 (1608 Metric) 1.5A 90mOhm
L3 | https://www.coilcraft.com/getmedia/97b6ad34-63ed-485c-a3ac-2a258e22c8ff/mintrans.pdf | 1 |  | Transformer | Coilcraft | Q4470-CL | Q4470-CL | miniature transformers were developed for use with
M2 | https://www.pololu.com/product/2858 | 1 |  | Module | Pololu Robotics & Electronics | D24V22F5 | D24V22F5 | DCDC Regulator Module 24-36V IN 5VDC OUT
M3 | https://www.pololu.com/product/2857 | 1 |  | Module | Pololu Robotics & Electronics | D24V22F5 | D24V22F3 | DCDC Regulator Module 24-36V IN 3.3VDC OUT
R1,R2,R3,R4,R6,R7 | https://www.yageo.com/upload/media/product/productsearch/datasheet/rchip/PYu-RC_Group_51_RoHS_L_10.pdf | 6 |  | Thick Film Resistor | Digikey | 311-1.00KLRTR-ND | 1K | kOhms ±1% 0.063W, 1/16W Chip Resistor 0402 (1005 Metric) Moisture Resistant Thick Film
R5,R11 | https://www.yageo.com/upload/media/product/productsearch/datasheet/rchip/PYu-RC_Group_51_RoHS_L_10.pdf | 2 |  | Thick FIlm Resistor | Digikey | 311-10.0KLRCT-ND | 10K | 10 kOhms ±1% 0.063W, 1/16W Chip Resistor 0402 (1005 Metric) Moisture Resistant Thick Film
R8,R9,R10,R12,R13,R14,R15,R16,R19,R41,R42 |  | 11 |  | SMT Chip Resistor | Digikey | 311-470HRCT-ND | 470r | RES SMD 470 OHM 1% 1/10W 0603
R17,R43 |  | 2 |  | SMT Chip Resistor | Digikey | 311-1.00MFRCT-ND | 1M | RES SMD 1M OHM 1% 1/4W 1206
R18,R22 | https://www.yageo.com/upload/media/product/productsearch/datasheet/rchip/PYu-RC_Group_51_RoHS_L_11.pdf | 2 |  | Resistor | Digikey | 311-22.0LRTR-ND | 22R | 22 Ohms ±1% 0.063W, 1/16W Chip Resistor 0402 (1005 Metric) Moisture Resistant Thick Film
R20,R21 | https://www.yageo.com/upload/media/product/products/datasheet/rchip/PYu-RC_Group_51_RoHS_L_12.pdf | 2 |  | Resistor | Digikey | 311-2.20KHRTR-ND | 2.2K | 2.2 kOhms ±1% 0.1W, 1/10W Chip Resistor 0603 (1608 Metric) Moisture Resistant Thick Film
R28,R29,R30,R31,R32,R33,R34,R35,R36,R37 | https://www.yageo.com/upload/media/product/products/datasheet/rchip/PYu-RC_Group_51_RoHS_L_12.pdf | 10 |  | Resistor | Digikey | 311-2.20KLRTR-ND | 2.2K | 2.2 kOhms ±1% 0.063W, 1/16W Chip Resistor 0402 (1005 Metric) Moisture Resistant Thick Film
R38 | https://www.yageo.com/upload/media/product/productsearch/datasheet/rchip/PYu-AC_51_RoHS_L_7.pdf | 1 |  | Thick Film Resistor | Digikey | YAG3440CT-ND | 120R | 120 Ohms ±1% 0.063W, 1/16W Chip Resistor 0402 (1005 Metric) Automotive AEC-Q200, Moisture Resistant Thick Film
R39,R40 | https://www.yageo.com/upload/media/product/app/datasheet/rchip/pyu-rt_1-to-0.01_rohs_l.pdf | 2 |  | Resistor | Digikey | YAG4498TR-ND | 1M | RES SMD 1M OHM 0.1% 1/10W 0603
SW1 | https://www.ckswitches.com/media/2779/pts636.pdf | 1 |  | Mechanical Switch | Digikey | CKN12310-2-ND | PTS636 SM43 SMTR LFS | Tactile Switch SPST-NO Top Actuated Surface Mount
U1 | https://www.st.com/resource/en/datasheet/stm32f446ve.pdf | 1
U4 | https://www.analog.com/media/en/technical-documentation/data-sheets/max3535e-mxl1535e.pdf | 1 |  | Integrated Circuit | Digikey | MAX3535ECWI+TTR-ND | MAX3535ECWI+T | 1/1 Transceiver Full RS422, RS485 28-SOIC
X1 | https://abracon.com/Resonators/abm3b.pdf | 1 |  | Crystal Oscillator | Digikey | 535-9720-2-ND | 8MHZ | 8MHz ±20ppm Crystal 18pF 200 Ohms 4-SMD, No Lead
X2 | https://abracon.com/Resonators/ABS07.pdf | 1 |  | Crystal Oscillator | Digikey | 535-9544-1-ND | 32.7680KHZ | 32.768kHz ±20ppm Crystal 9pF 70 kOhms 2-SMD, No Lead

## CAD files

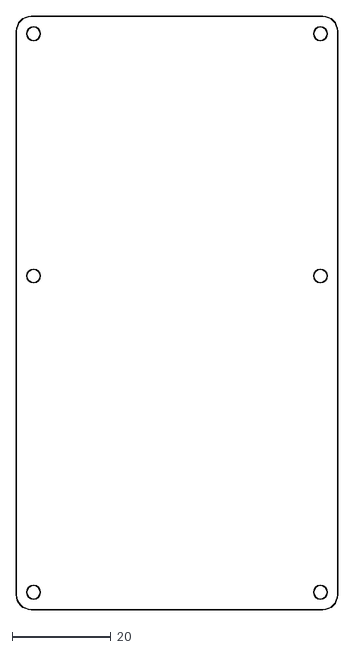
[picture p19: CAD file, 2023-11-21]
PCB/depreciated/JoyStick-Hat-V2/JoyStick_Board_Shape_NoNotch120mm.dxf
65.0 x 120.0

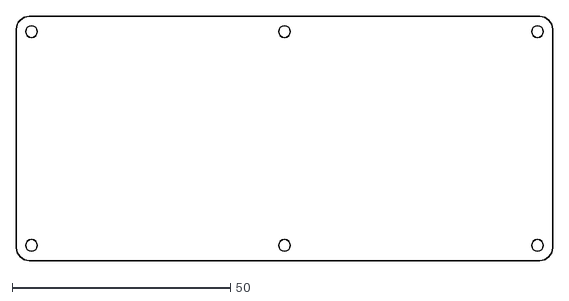
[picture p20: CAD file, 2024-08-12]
PCB/JoyStick-Hat-V2-Re-Imagined/JoyStick_Hat_V2_Shape.dxf
123.0 x 56.0

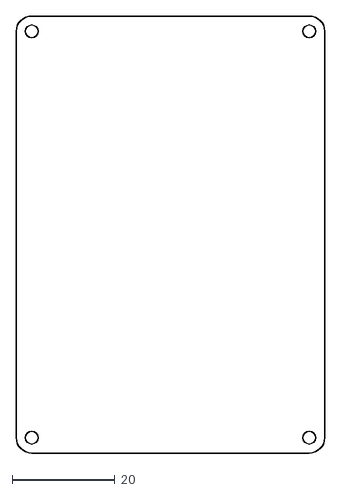
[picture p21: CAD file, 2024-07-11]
PCB/LED_Driver_HUD/LED_Board_Shape.dxf
60.0 x 85.0

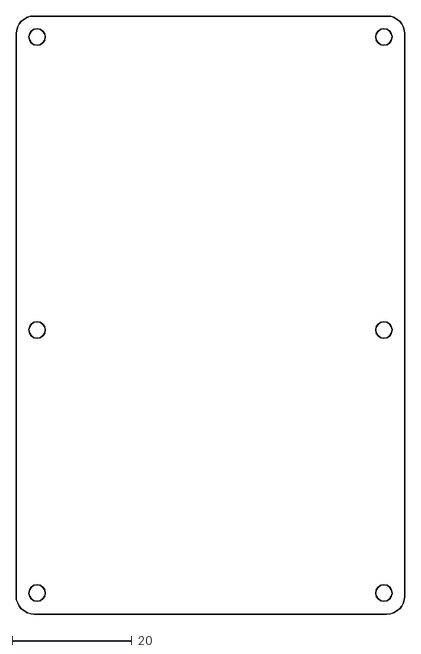
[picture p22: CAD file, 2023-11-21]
PCB/depreciated/JoyStick-Hat-V2/Joy_Stick_Hat_Board_Shape_NoNotch.dxf
65.0 x 100.0

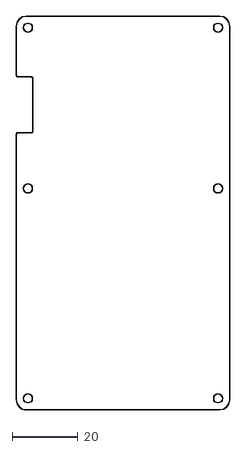
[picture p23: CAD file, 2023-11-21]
PCB/depreciated/JoyStick-Hat-V2/Joystick_Hat_Board_Shape_120mm.dxf
65.0 x 120.0

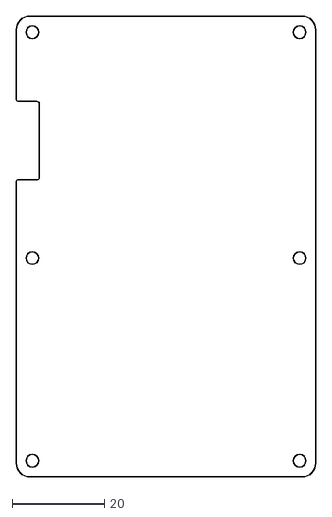
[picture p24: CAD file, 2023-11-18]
PCB/depreciated/JoyStick-Hat-V2/Joystick_Hat_Board_shape.dxf
65.0 x 100.0

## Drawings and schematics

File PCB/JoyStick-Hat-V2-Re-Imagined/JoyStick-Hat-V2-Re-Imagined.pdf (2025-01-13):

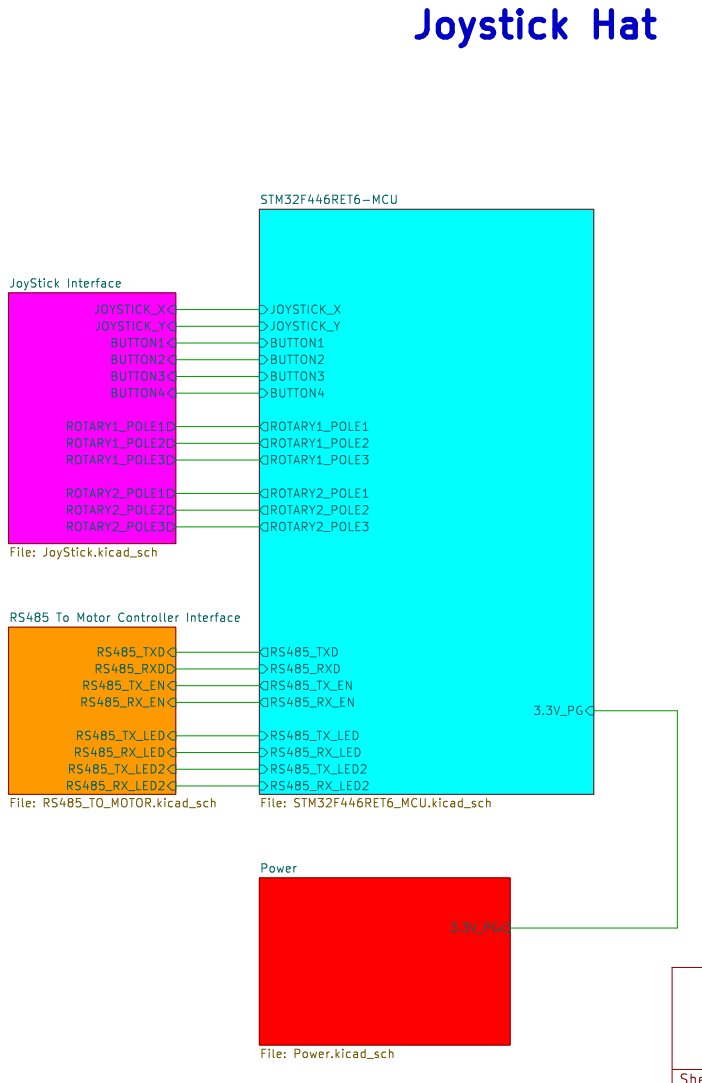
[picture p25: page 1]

JoyStick Interface File: JoyStick.kicad_sch RS485_TX_EN
ROTARY2_POLE3 ROTARY1_POLE1 ROTARY1_POLE2 ROTARY1_POLE3 ROTARY2_POLE2 ROTARY2_POLE1 RS485_TX_LED

Id: 1/5 Title: File: JoyStick-Hat-V2-Re-Imagined.kicad_sch Sheet: / 3.3V_PG

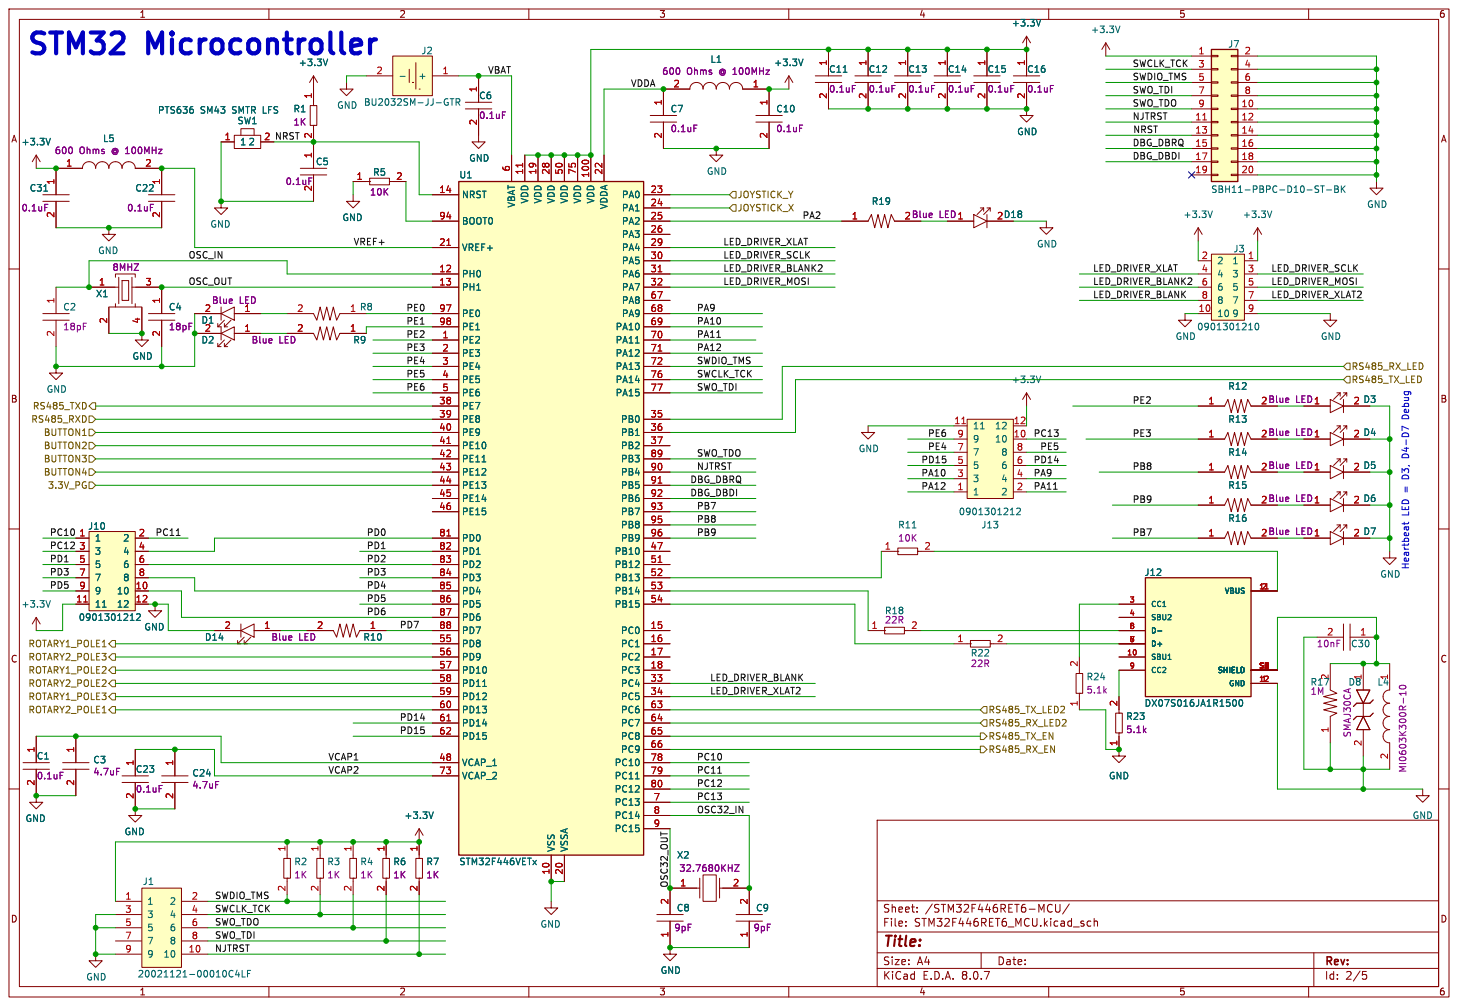
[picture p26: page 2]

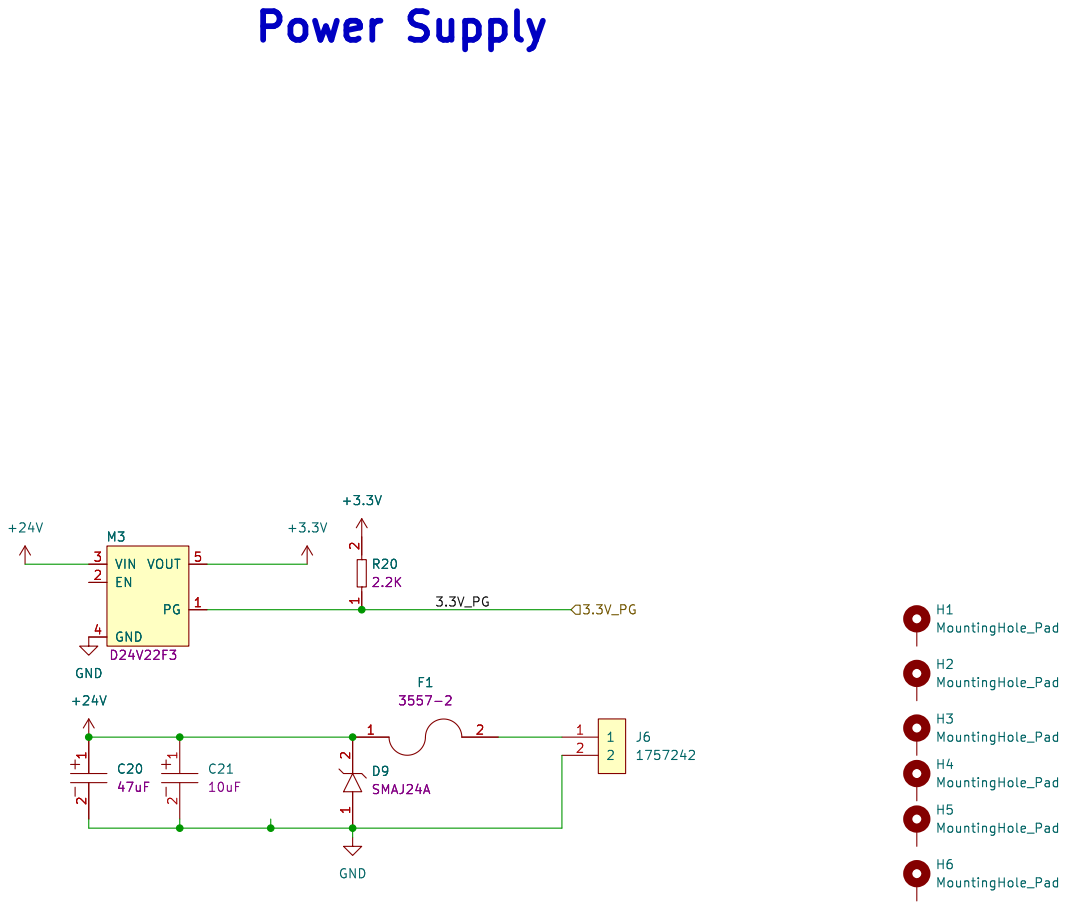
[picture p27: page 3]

1 2 GND M3D24V22F3PG 1 EN 2 VIN 3 GND 4 VOUT 5 +24V

Id: 5/5 Title: File: Power.kicad_sch Sheet: /Power/

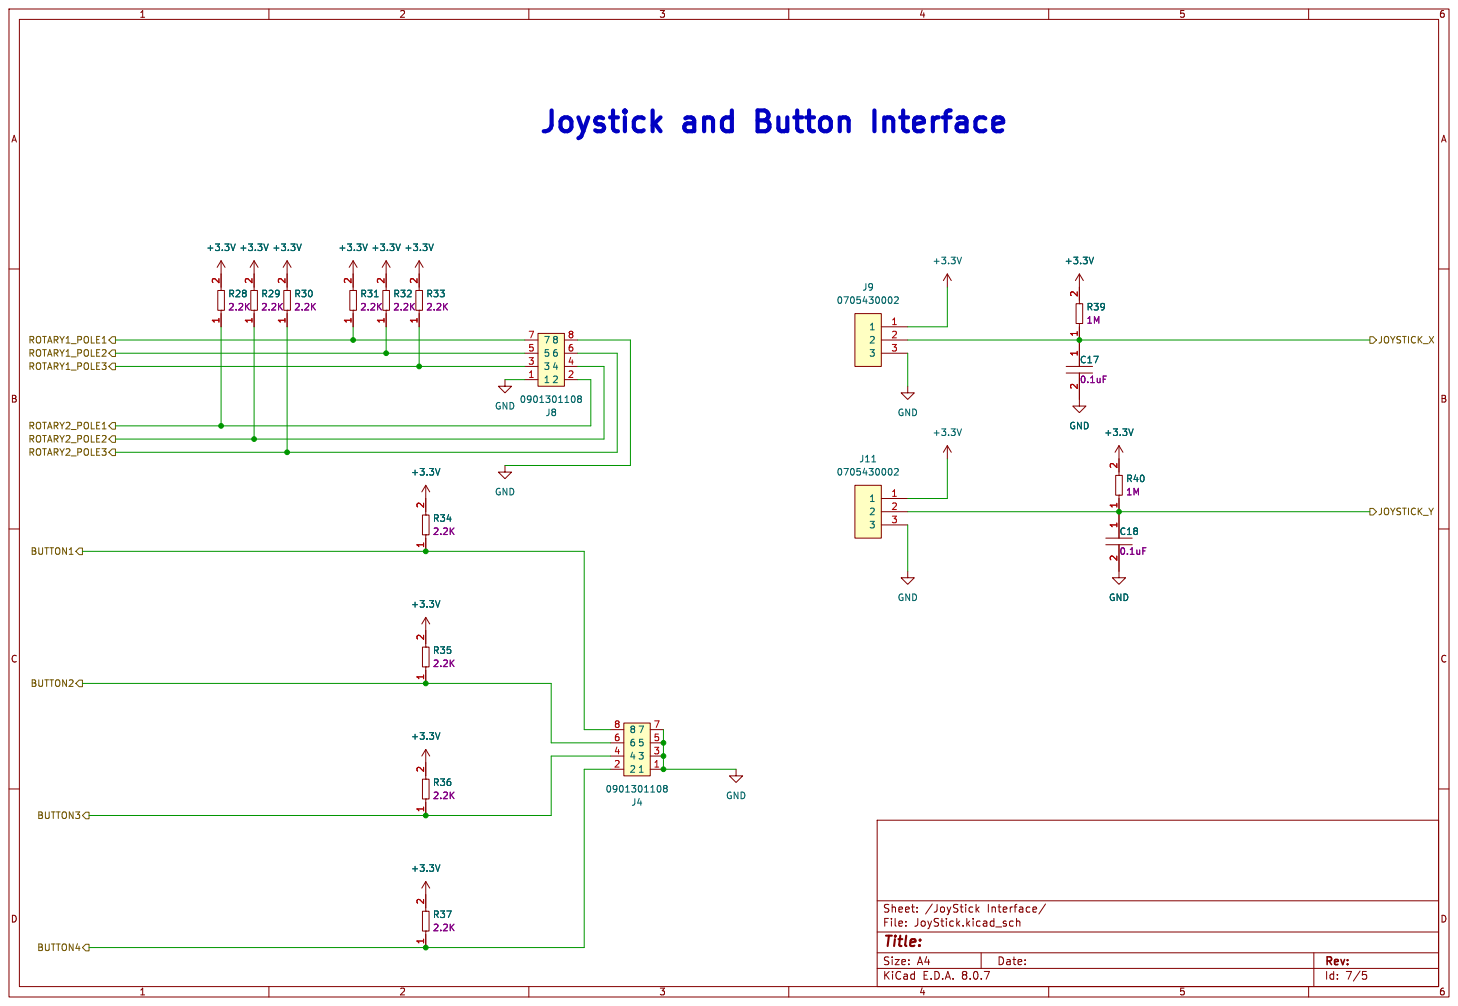
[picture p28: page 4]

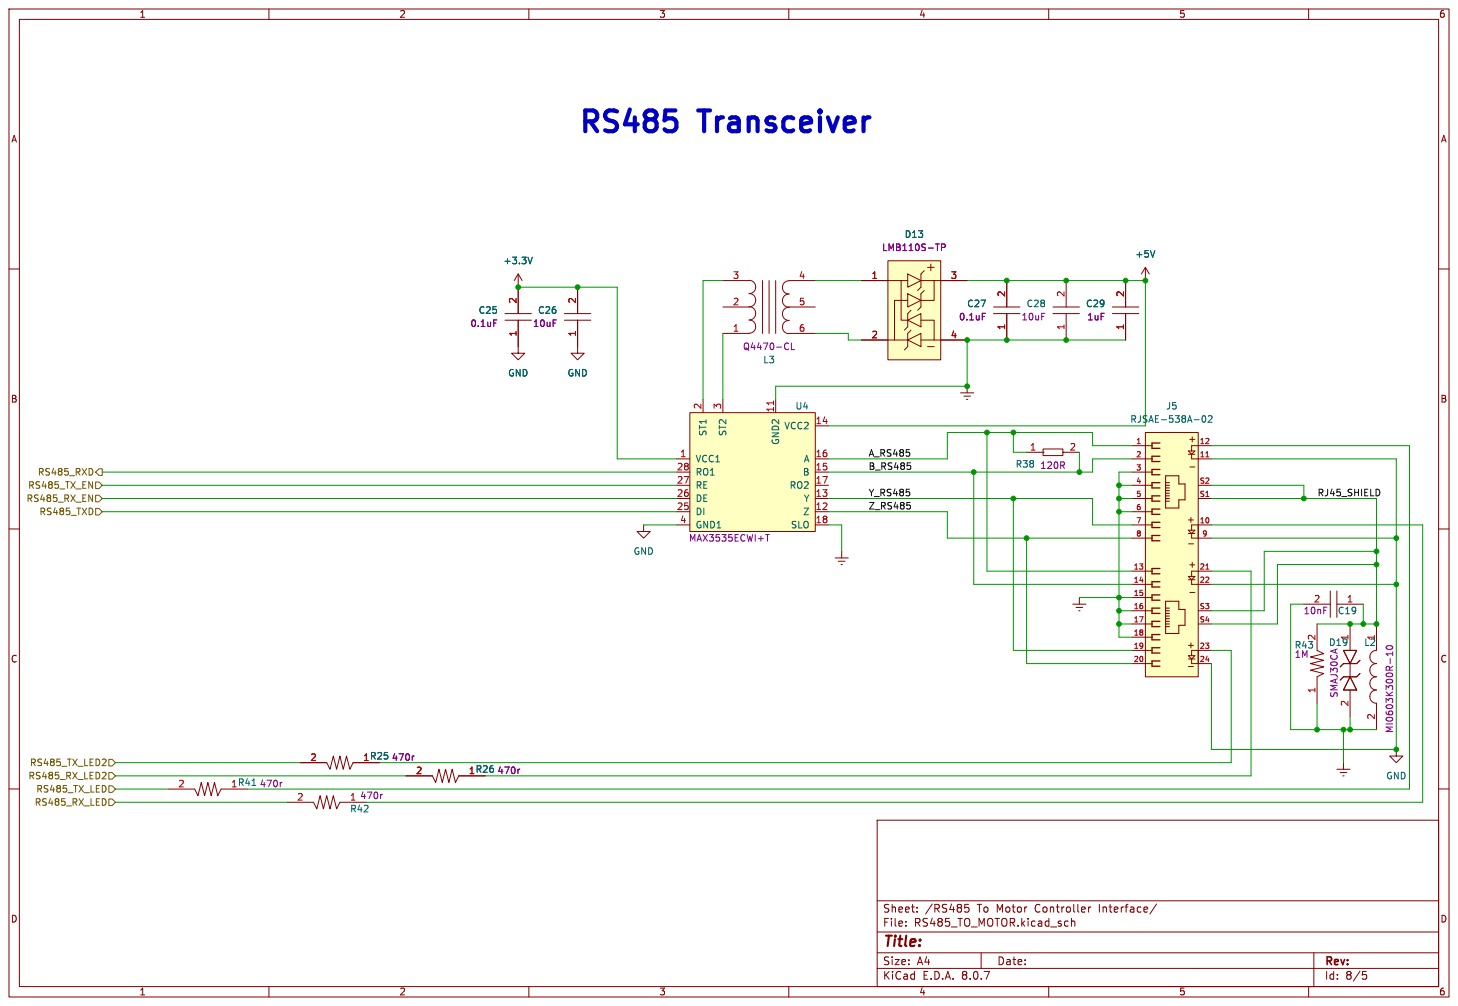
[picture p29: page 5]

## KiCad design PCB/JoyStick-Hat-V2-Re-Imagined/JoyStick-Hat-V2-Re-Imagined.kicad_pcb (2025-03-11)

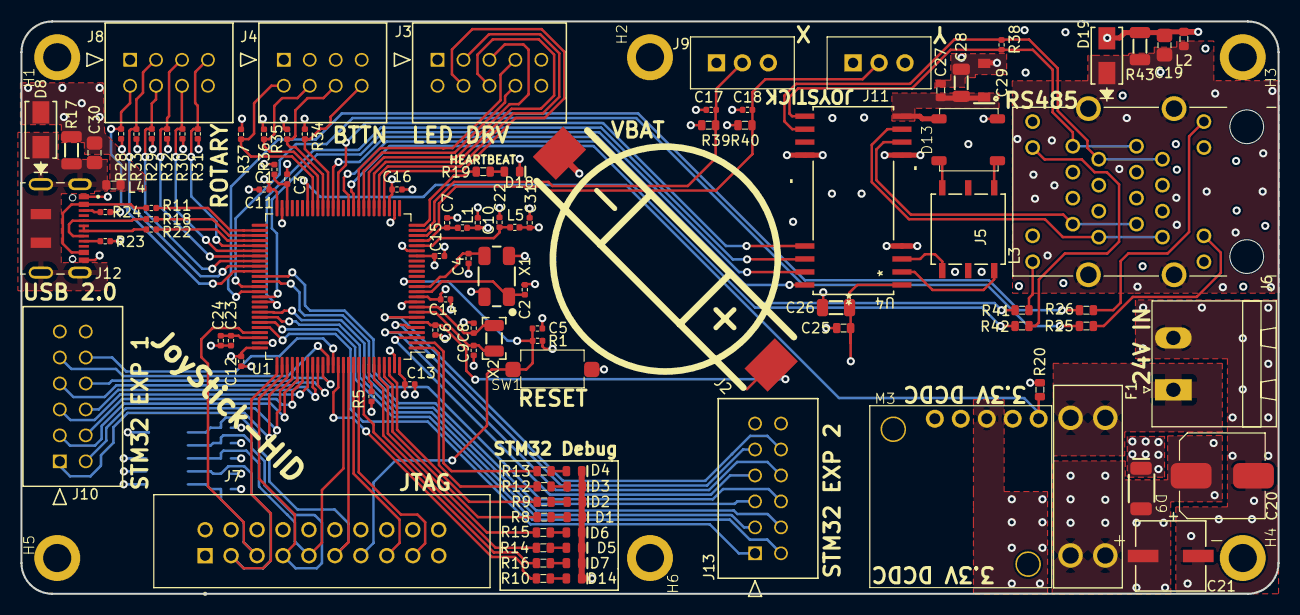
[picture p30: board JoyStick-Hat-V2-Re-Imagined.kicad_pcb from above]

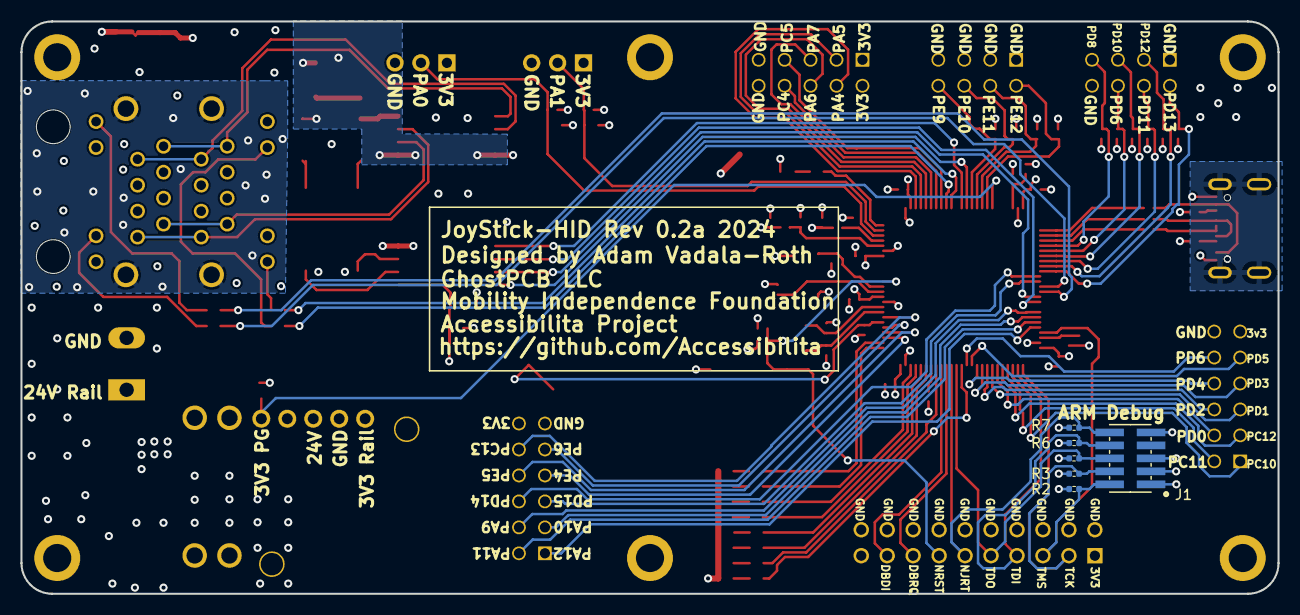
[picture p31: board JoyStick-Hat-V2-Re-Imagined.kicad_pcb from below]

Board: 4 copper layers, 123.0 x 56.0 mm, 116 parts (6 on the bottom side), 111 nets.

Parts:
C1, C5, C6, C7, C10, C11, C12, C13, C14, C15, C16, C17, C18, C22, C23, C31: C0402C104K9PACTU; R0402
C2, C4: GCM1555C1H180GA16D; C0402
C3, C24: GRM155R60J475ME47D; C0402
C8, C9: CL05C090CB5NNNC; C0402
C19, C30: C0805C103KCRACAUTO; C0805
C20: UUQ1H470MCL1GS; CP_Elec_8x10
C21: UUQ1H100MCL1GB; CAP_UUQ_6P3X5P4_NCH
C25, C27: CL10B104JB8NNNC; C0603
C26, C28: CGA5L3X5R1V106K160AB; C1206
C29: C1206C105K3RACAUTO; D_SOD-123
D1, D2, D3, D4, D5, D6, D7, D14, D18: LTST-C194TBKT; LED0603
D8, D19: SMAJ30CA
D9: SMAJ24A; SMAJ
D13: LMB110S-TP
F1: 3557-2; FUSE_3557-2
H1, H2, H3, H4, H5, H6: MountingHole_Pad; RPI_HAT_HOLE
J1: 20021121-00010C4LF
J2: BU2032SM-JJ-GTR
J3: 0901301210; CON_901301210_MOL
J4, J8: 0901301108; CON_901301108_MOL
J5: RJSAE-538A-02; AMPHENOL_RJSAE538A02
J6: 1757242; PhoenixContact_MSTBA-G_02x5.08mm_Angled
J7: SBH11-PBPC-D10-ST-BK; SULLINS_SBH11-PBPC-D10-ST-BK
J9, J11: 0705430002; Shrouded_Pin_Header_Straight_1x03_Pitch2.54mm
J10, J13: 0901301212; CON_901301212_MOL
J12: DX07S016JA1R1500; JAE_DX07S016JA1R1500
L1, L5: BLM15HG601SN1D
L2, L4: MI0603K300R-10
L3: Q4470-CL; SO6_Q4470-CL_C-SIZE_COC
M3: D24V22F3; D24V22F12
R1, R2, R3, R4, R6, R7: RC0402FR-071KL; R0402
R5, R11: RC0402FR-0710KL; R0402
R8, R9, R10, R12, R13, R14, R15, R16, R19, R25, R26, R41, R42: RC0603FR-07470RL; R0603
R17, R43: RC1206FR-071ML; R1206
R18, R22: RC0402FR-0722RL; R0402
R20: RC0603FR-072K2L; R0603
R23, R24: RC0402FR-075K1L; R0402
R28, R29, R30, R31, R32, R33, R34, R35, R36, R37: RC0402FR-072K2L; R0402
R38: AC0402FR-07120RL; R0402
R39, R40: RT0603BRD071ML; R0603
SW1: PTS636 SM43 SMTR LFS
U1: STM32F446VETx; LQFP-100_14x14mm_P0.5mm
U4: MAX3535ECWI+T; 21-0145_W28M&plus_9_MXM
X1: ABM3B-8.000MHZ-B2-T; ABM3B8.000MHZB2T
X2: ABS07-32.768KHZ-9-T

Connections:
+3.3V: C10.1, C11.1, C12.1, C13.1, C14.1, C15.1, C16.1, C25.2, C26.2, C31.1, J1.1, J3.1, J3.2, J7.1, J9.1, J10.11, J11.1, J13.12, L1.1, L5.1, M3.5 (VOUT), R1.1, R2.1, R3.1, R4.1, R6.1, R7.1, R20.2, R28.2, R29.2, R30.2, R31.2, R32.2, R33.2, R34.2, R35.2, R36.2, R37.2, R39.2, R40.2, U1.11 (VDD), U1.19 (VDD), U1.28 (VDD), U1.50 (VDD), U1.75 (VDD), U1.100 (VDD), U4.1 (VCC1)
+5V: C27.2, C28.2, C29.2, D13.3, U4.14 (VCC2)
+24V: C20.1, C21.1, D9.2, F1.1, M3.3 (VIN)
/JoyStick Interface/BUTTON1: J4.8, R34.1, U1.40 (PE9)
/JoyStick Interface/BUTTON2: J4.6, R35.1, U1.41 (PE10)
/JoyStick Interface/BUTTON3: J4.4, R36.1, U1.42 (PE11)
/JoyStick Interface/BUTTON4: J4.2, R37.1, U1.43 (PE12)
/JoyStick Interface/JOYSTICK_X: C17.1, J9.2, R39.1, U1.24 (PA1)
/JoyStick Interface/JOYSTICK_Y: C18.1, J11.2, R40.1, U1.23 (PA0)
/JoyStick Interface/ROTARY1_POLE1: J8.7, R31.1, U1.55 (PD8)
/JoyStick Interface/ROTARY1_POLE2: J8.5, R32.1, U1.57 (PD10)
/JoyStick Interface/ROTARY1_POLE3: J8.3, R33.1, U1.59 (PD12)
/JoyStick Interface/ROTARY2_POLE1: J8.2, R28.1, U1.60 (PD13)
/JoyStick Interface/ROTARY2_POLE2: J8.4, R29.1, U1.58 (PD11)
/JoyStick Interface/ROTARY2_POLE3: J8.6, R30.1, U1.56 (PD9)
/Power/3.3V_PG: M3.1 (PG), R20.1, U1.44 (PE13)
/RS485 To Motor Controller Interface/A_RS485: J5.1, J5.13, R38.1, U4.16 (A)
/RS485 To Motor Controller Interface/B_RS485: J5.2, J5.14, R38.2, U4.15 (B)
/RS485 To Motor Controller Interface/RJ45_SHIELD: C19.1, D19.1, J5.S1, J5.S2, J5.S3, J5.S4, L2.1, R43.2
/RS485 To Motor Controller Interface/RS485_RXD: U1.39 (PE8), U4.28 (RO1)
/RS485 To Motor Controller Interface/RS485_RX_EN: U1.66 (PC9), U4.26 (DE)
/RS485 To Motor Controller Interface/RS485_RX_LED: R42.2, U1.35 (PB0)
/RS485 To Motor Controller Interface/RS485_RX_LED2: R26.2, U1.64 (PC7)
/RS485 To Motor Controller Interface/RS485_TXD: U1.38 (PE7), U4.25 (DI)
/RS485 To Motor Controller Interface/RS485_TX_EN: U1.65 (PC8), U4.27 (RE)
/RS485 To Motor Controller Interface/RS485_TX_LED: R41.2, U1.36 (PB1)
/RS485 To Motor Controller Interface/RS485_TX_LED2: R25.2, U1.63 (PC6)
/RS485 To Motor Controller Interface/Y_RS485: J5.7, J5.19, U4.13 (Y)
/RS485 To Motor Controller Interface/Z_RS485: J5.8, J5.20, U4.12 (Z)
/STM32F446RET6-MCU/DBG_DBDI: J7.17, U1.92 (PB6)
/STM32F446RET6-MCU/DBG_DBRQ: J7.15, U1.91 (PB5)
/STM32F446RET6-MCU/LED_DRIVER_BLANK: J3.8, U1.33 (PC4)
/STM32F446RET6-MCU/LED_DRIVER_BLANK2: J3.6, U1.31 (PA6)
/STM32F446RET6-MCU/LED_DRIVER_MOSI: J3.5, U1.32 (PA7)
/STM32F446RET6-MCU/LED_DRIVER_SCLK: J3.3, U1.30 (PA5)
/STM32F446RET6-MCU/LED_DRIVER_XLAT: J3.4, U1.29 (PA4)
/STM32F446RET6-MCU/LED_DRIVER_XLAT2: J3.7, U1.34 (PC5)
/STM32F446RET6-MCU/NJTRST: J1.10, J7.11, R7.2, U1.90 (PB4)
/STM32F446RET6-MCU/NRST: C5.1, J7.13, R1.2, SW1.2, U1.14 (NRST)
/STM32F446RET6-MCU/OSC32_IN: C9.2, U1.8 (PC14), X2.2
/STM32F446RET6-MCU/OSC32_OUT: C8.2, U1.9 (PC15), X2.1
/STM32F446RET6-MCU/OSC_IN: C2.1, U1.12 (PH0), X1.1
/STM32F446RET6-MCU/OSC_OUT: C4.1, U1.13 (PH1), X1.3
/STM32F446RET6-MCU/PA2: R19.1, U1.25 (PA2)
/STM32F446RET6-MCU/PA9: J13.4, U1.68 (PA9)
/STM32F446RET6-MCU/PA10: J13.3, U1.69 (PA10)
/STM32F446RET6-MCU/PA11: J13.2, U1.70 (PA11)
/STM32F446RET6-MCU/PA12: J13.1, U1.71 (PA12)
/STM32F446RET6-MCU/PB7: R16.1, U1.93 (PB7)
/STM32F446RET6-MCU/PB8: R14.1, U1.95 (PB8)
/STM32F446RET6-MCU/PB9: R15.1, U1.96 (PB9)
/STM32F446RET6-MCU/PC10: J10.1, U1.78 (PC10)
/STM32F446RET6-MCU/PC11: J10.2, U1.79 (PC11)
/STM32F446RET6-MCU/PC12: J10.3, U1.80 (PC12)
/STM32F446RET6-MCU/PC13: J13.10, U1.7 (PC13)
/STM32F446RET6-MCU/PD0: J10.4, U1.81 (PD0)
/STM32F446RET6-MCU/PD1: J10.5, U1.82 (PD1)
/STM32F446RET6-MCU/PD2: J10.6, U1.83 (PD2)
/STM32F446RET6-MCU/PD3: J10.7, U1.84 (PD3)
/STM32F446RET6-MCU/PD4: J10.8, U1.85 (PD4)
/STM32F446RET6-MCU/PD5: J10.9, U1.86 (PD5)
/STM32F446RET6-MCU/PD6: J10.10, U1.87 (PD6)
/STM32F446RET6-MCU/PD7: R10.1, U1.88 (PD7)
/STM32F446RET6-MCU/PD14: J13.6, U1.61 (PD14)
/STM32F446RET6-MCU/PD15: J13.5, U1.62 (PD15)
/STM32F446RET6-MCU/PE0: R8.1, U1.97 (PE0)
/STM32F446RET6-MCU/PE1: R9.1, U1.98 (PE1)
/STM32F446RET6-MCU/PE2: R12.1, U1.1 (PE2)
/STM32F446RET6-MCU/PE3: R13.1, U1.2 (PE3)
/STM32F446RET6-MCU/PE4: J13.7, U1.3 (PE4)
/STM32F446RET6-MCU/PE5: J13.8, U1.4 (PE5)
/STM32F446RET6-MCU/PE6: J13.9, U1.5 (PE6)
/STM32F446RET6-MCU/SWCLK_TCK: J1.4, J7.3, R3.2, U1.76 (PA14)
/STM32F446RET6-MCU/SWDIO_TMS: J1.2, J7.5, R2.2, U1.72 (PA13)
/STM32F446RET6-MCU/SWO_TDI: J1.8, J7.7, R6.2, U1.77 (PA15)
/STM32F446RET6-MCU/SWO_TDO: J1.6, J7.9, R4.2, U1.89 (PB3)
/STM32F446RET6-MCU/VBAT: C6.1, J2.1 (+), U1.6 (VBAT)
/STM32F446RET6-MCU/VCAP1: C1.1, C3.1, U1.48 (VCAP_1)
/STM32F446RET6-MCU/VCAP2: C23.1, C24.1, U1.73 (VCAP_2)
/STM32F446RET6-MCU/VDDA: C7.1, L1.2, U1.22 (VDDA)
/STM32F446RET6-MCU/VREF+: C22.1, L5.2, U1.21 (VREF+)
Earth: C19.2, C27.1, C28.1, C29.1, D13.4, D19.2, J5.3, J5.4, J5.5, J5.6, J5.15, J5.16, J5.17, J5.18, L2.2, R43.1, U4.11 (GND2), U4.18 (SLO)
GND: C1.2, C2.2, C3.2, C4.2, C5.2, C6.2, C7.2, C8.1, C9.1, C10.2, C11.2, C12.2, C13.2, C14.2, C15.2, C16.2, C17.2, C18.2, C20.2, C21.2, C22.2, C23.2, C24.2, C25.1, C26.1, C30.2, C31.2, D1.2, D2.2, D3.2, D4.2, D5.2, D6.2, D7.2, D8.2, D9.1, D14.2, D18.2, J1.3, J1.5, J1.9, J2.2 (-), J3.9, J3.10, J4.1, J4.3, J4.5, J4.7, J5.9, J5.11, J5.22, J5.24, J6.2, J7.2, J7.4, J7.6, J7.8, J7.10, J7.12, J7.14, J7.16, J7.18, J7.20, J8.1, J8.8, J9.3, J10.12, J11.3, J12.1 (GND), J12.12 (GND), J13.11, L4.2, M3.4 (GND), R5.1, R17.1, R23.1, R24.1, SW1.1, U1.10 (VSS), U1.20 (VSSA), U1.27 (VSS), U1.49 (VSS), U1.74 (VSS), U1.99 (VSS), U4.4 (GND1), X1.2, X1.4
unnamed: C30.1, D8.1, J12.S1 (SHIELD), J12.S2 (SHIELD), J12.S3 (SHIELD), J12.S4 (SHIELD), J12.S5 (SHIELD), J12.S6 (SHIELD), L4.1, R17.2
unnamed: D1.1, R8.2
unnamed: D2.1, R9.2
unnamed: D3.1, R12.2
unnamed: D4.1, R13.2
unnamed: D5.1, R14.2
unnamed: D6.1, R15.2
unnamed: D7.1, R16.2
unnamed: D13.1, L3.4
unnamed: D13.2, L3.6
unnamed: D14.1, R10.2
unnamed: D18.1, R19.2
unnamed: F1.2, J6.1
unnamed: J5.10, R42.1
unnamed: J5.12, R41.1
unnamed: J5.21, R26.1
unnamed: J5.23, R25.1
unnamed: J12.3 (CC1), R24.2
unnamed: J12.9 (CC2), R23.2
unnamed: J12.6 (D+), J12.7 (D+), R22.2
unnamed: J12.5 (D-), J12.8 (D-), R18.2
unnamed: J12.2 (VBUS), J12.11 (VBUS), R11.2
unnamed: R5.2, U1.94 (BOOT0)
unnamed: R11.1, U1.52 (PB13)
unnamed: R18.1, U1.53 (PB14)
unnamed: R22.1, U1.54 (PB15)
unnamed: L3.3, U4.2 (ST1)
unnamed: L3.1, U4.3 (ST2)

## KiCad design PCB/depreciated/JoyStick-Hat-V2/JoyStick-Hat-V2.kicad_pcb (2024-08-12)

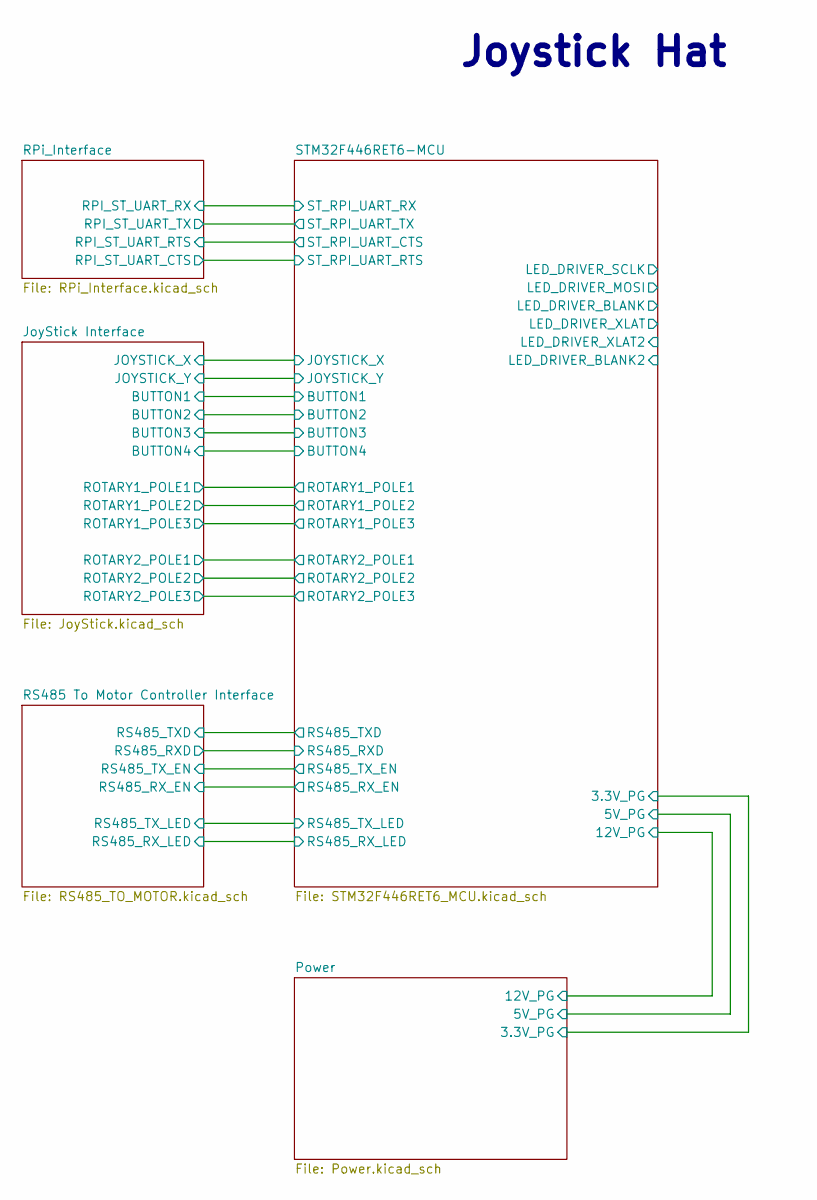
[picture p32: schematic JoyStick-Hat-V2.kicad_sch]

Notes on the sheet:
Joystick Hat

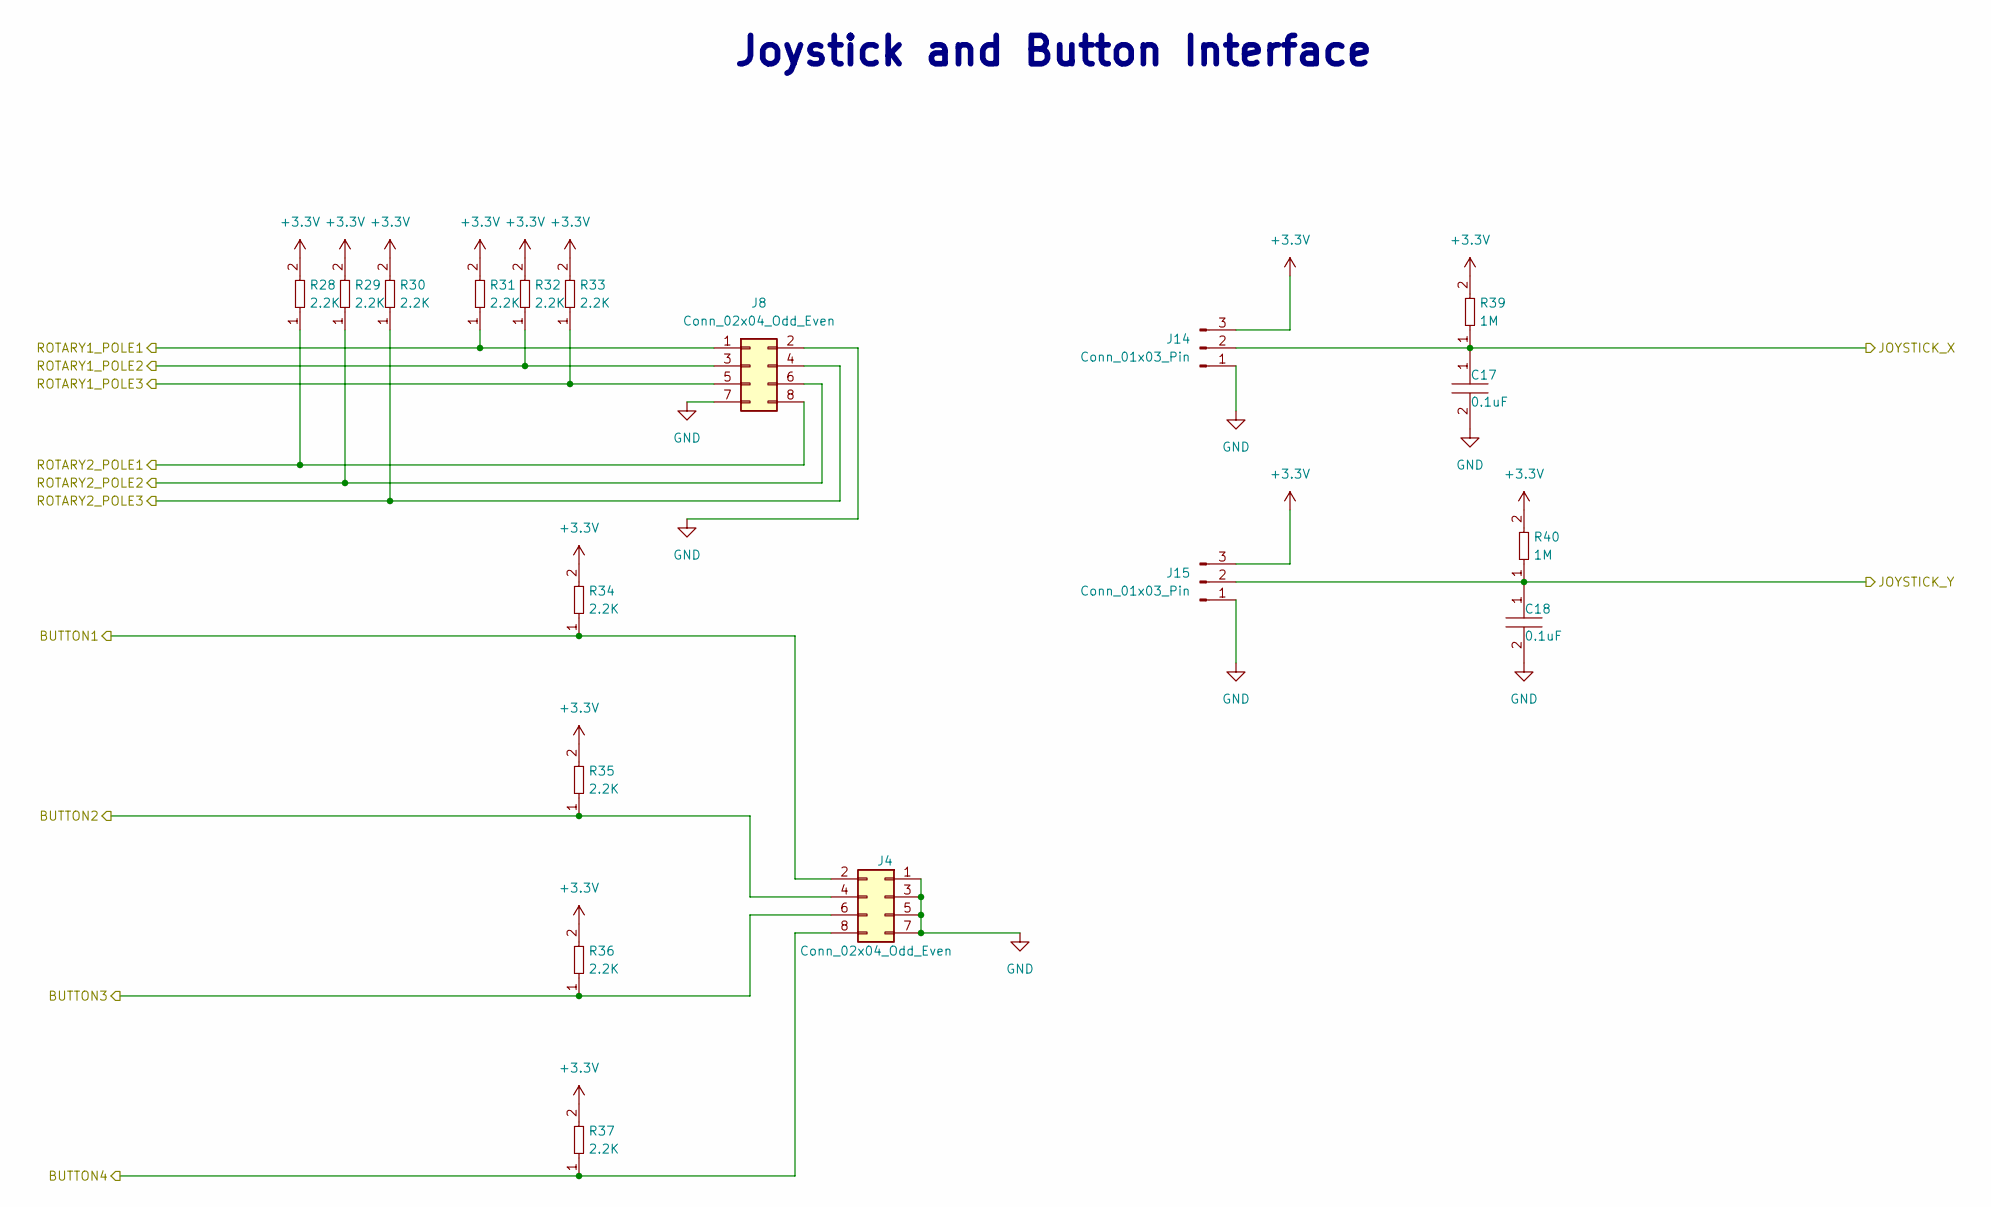
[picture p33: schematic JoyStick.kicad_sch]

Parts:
C17, C18: C0402C104K9PACTU; R0402; Tolerance 10%; Voltage 6.3V; MFR# C0402C104K9PACTU
J4, J8: Conn_02x04_Odd_Even; PinHeader_2x04_P2.54mm_Vertical
J14, J15: Conn_01x03_Pin; PinHeader_1x03_P2.54mm_Vertical
R28, R29, R30, R31, R32, R33, R34, R35, R36, R37: RC0402FR-072K2L; R0402; Tolerance 1%; Voltage N/A; MFR# RC0402FR-072K2L
R39, R40: RT0603BRD071ML; R0603; Tolerance 1%; Voltage N/A; MFR# RT0603BRD071ML

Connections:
+3.3V: J14.3, J15.3, R28.2, R29.2, R30.2, R31.2, R32.2, R33.2, R34.2, R35.2, R36.2, R37.2, R39.2, R40.2; also elsewhere on the board
/JoyStick Interface/BUTTON1: J4.2, R34.1; also elsewhere on the board
/JoyStick Interface/BUTTON2: J4.4, R35.1; also elsewhere on the board
/JoyStick Interface/BUTTON3: J4.6, R36.1; also elsewhere on the board
/JoyStick Interface/BUTTON4: J4.8, R37.1; also elsewhere on the board
/JoyStick Interface/JOYSTICK_X: C17.1, J14.2, R39.1; also elsewhere on the board
/JoyStick Interface/JOYSTICK_Y: C18.1, J15.2, R40.1; also elsewhere on the board
/JoyStick Interface/ROTARY1_POLE1: J8.1, R31.1; also elsewhere on the board
/JoyStick Interface/ROTARY1_POLE2: J8.3, R32.1; also elsewhere on the board
/JoyStick Interface/ROTARY1_POLE3: J8.5, R33.1; also elsewhere on the board
/JoyStick Interface/ROTARY2_POLE1: J8.8, R28.1; also elsewhere on the board
/JoyStick Interface/ROTARY2_POLE2: J8.6, R29.1; also elsewhere on the board
/JoyStick Interface/ROTARY2_POLE3: J8.4, R30.1; also elsewhere on the board
GND: C17.2, C18.2, J4.1, J4.3, J4.5, J4.7, J8.2, J8.7, J14.1, J15.1; also elsewhere on the board

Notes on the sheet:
Joystick and Button Interface

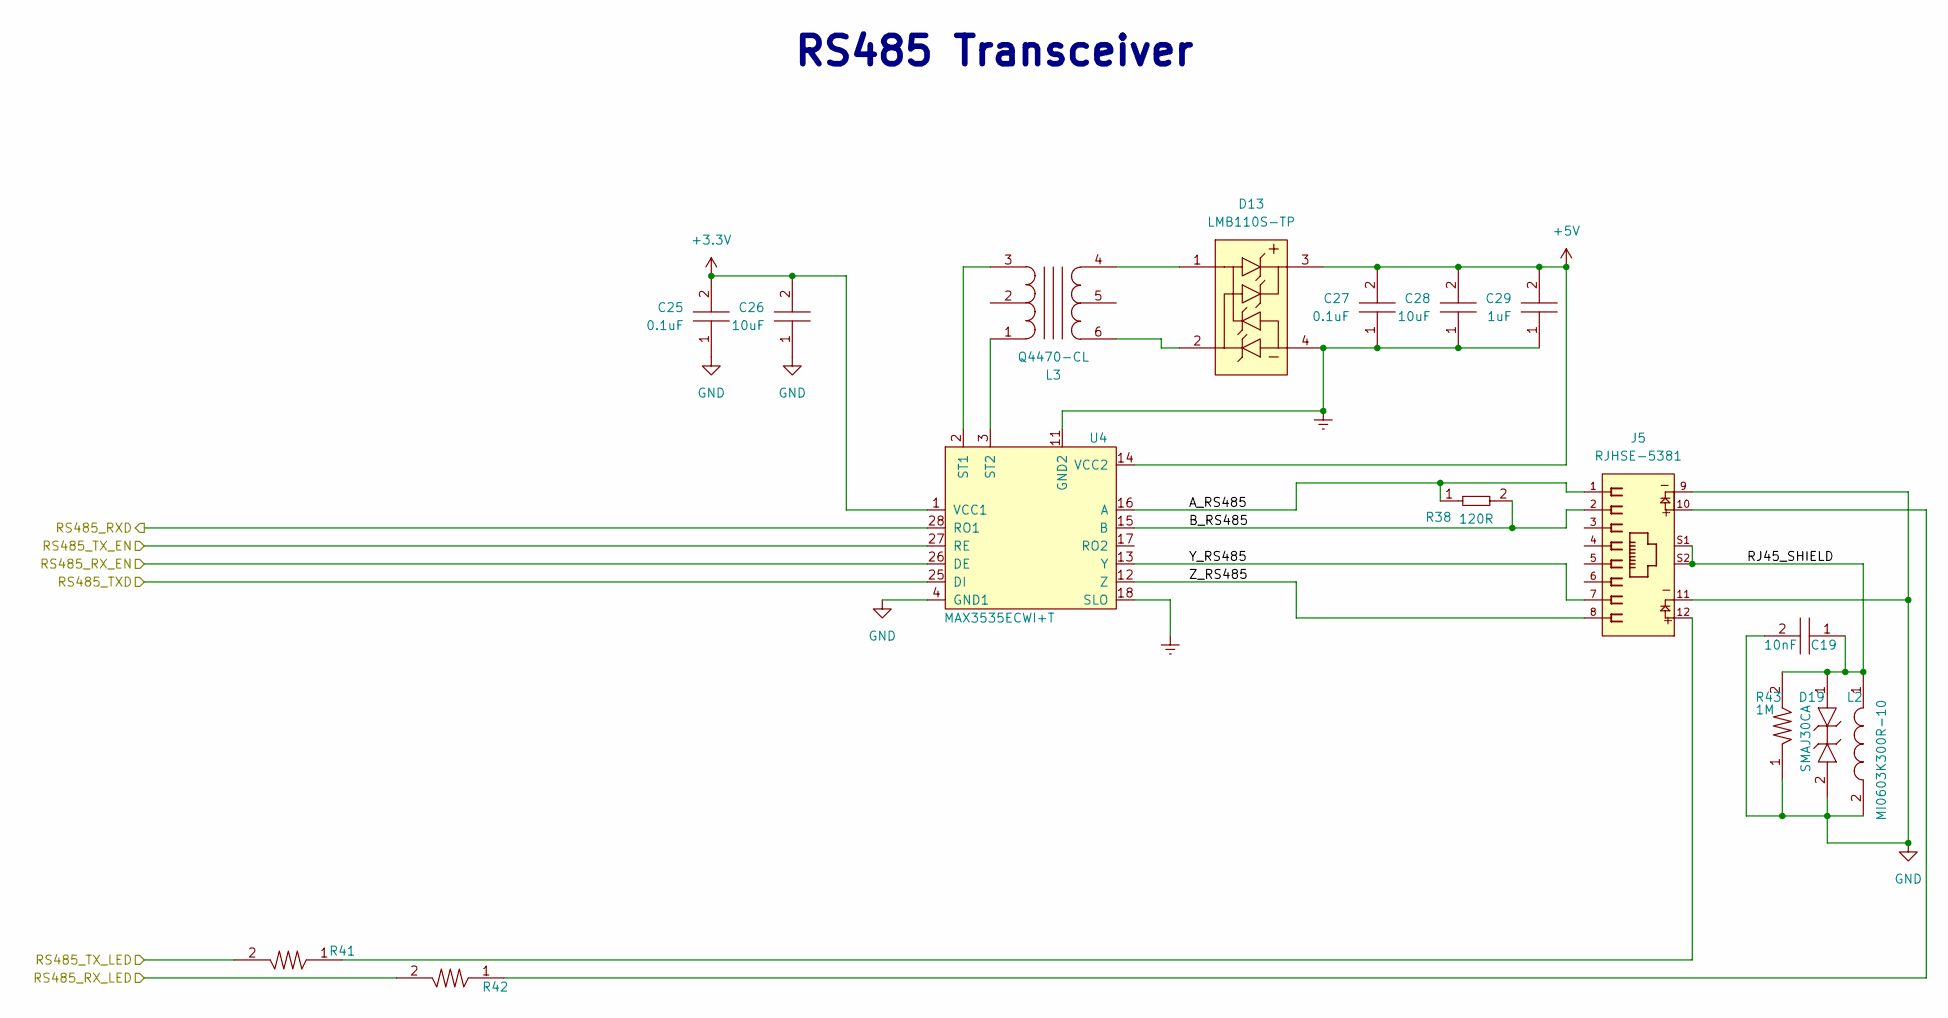
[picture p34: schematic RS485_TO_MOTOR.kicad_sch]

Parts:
C19: C0805C103KCRACAUTO; C0805; Tolerance 10%; Voltage 500V; MFR# C0805C103KCRACAUTO
C25, C27: CL10B104JB8NNNC; C0603; Tolerance 5%; Voltage 50V; MFR# CL10B104JB8NNNC
C26, C28: CGA5L3X5R1V106K160AB; C1206; Tolerance 10%; Voltage 35V; MFR# CGA5L3X5R1V106K160AB
C29: C1206C105K3RACAUTO; D_SOD-123; Tolerance 10%; Voltage 25V; MFR# C1206C105K3RACAUTO
D13: LMB110S-TP; Tolerance *; Voltage 850 mV @ 500 mA; MFR# LMB110S-TP
D19: SMAJ30CA; Tolerance *; Voltage 30V Clamp; MFR# SMAJ30CA
J5: RJHSE-5381; AMPHENOL_RJHSE-5381; Tolerance *; Voltage *; MFR# RJHSE-5381
L2: MI0603K300R-10; Tolerance *; Voltage *; MFR# MI0603K300R-10
L3: Q4470-CL; SO6_Q4470-CL_C-SIZE_COC; Tolerance *; Voltage 5V; MFR# Q4470-CL
R38: AC0402FR-07120RL; R0402; Tolerance 1%; Voltage *; MFR# AC0402FR-07120RL
R41, R42: RC0603FR-07470RL; R0603; Tolerance 1%; Voltage *; MFR# RC0603FR-07470RL
R43: RC1206FR-071ML; R1206; Tolerance 1%; Voltage *; MFR# RC1206FR-071ML
U4: MAX3535ECWI+T; 21-0145_W28M&plus_9_MXM; Tolerance N/A; Voltage 3-5.5V; MFR# MAX3535ECWI+T

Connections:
+3.3V: C25.2, C26.2, U4.1 (VCC1); also elsewhere on the board
+5V: C27.2, C28.2, C29.2, D13.3, U4.14 (VCC2); also elsewhere on the board
/RS485 To Motor Controller Interface/A_RS485: J5.1, R38.1, U4.16 (A)
/RS485 To Motor Controller Interface/B_RS485: J5.2, R38.2, U4.15 (B)
/RS485 To Motor Controller Interface/RJ45_SHIELD: C19.1, D19.1, J5.S1, J5.S2, L2.1, R43.2
/RS485 To Motor Controller Interface/RS485_RXD: U4.28 (RO1); also elsewhere on the board
/RS485 To Motor Controller Interface/RS485_RX_EN: U4.26 (DE); also elsewhere on the board
/RS485 To Motor Controller Interface/RS485_RX_LED: R42.2; also elsewhere on the board
/RS485 To Motor Controller Interface/RS485_TXD: U4.25 (DI); also elsewhere on the board
/RS485 To Motor Controller Interface/RS485_TX_EN: U4.27 (RE); also elsewhere on the board
/RS485 To Motor Controller Interface/RS485_TX_LED: R41.2; also elsewhere on the board
/RS485 To Motor Controller Interface/Y_RS485: J5.7, U4.13 (Y)
/RS485 To Motor Controller Interface/Z_RS485: J5.8, U4.12 (Z)
Earth: C27.1, C28.1, C29.1, D13.4, U4.11 (GND2), U4.18 (SLO)
GND: C19.2, C25.1, C26.1, D19.2, J5.9, J5.11, L2.2, R43.1, U4.4 (GND1); also elsewhere on the board
unnamed: D13.1, L3.4
unnamed: D13.2, L3.6
unnamed: J5.10, R42.1
unnamed: J5.12, R41.1
unnamed: L3.3, U4.2 (ST1)
unnamed: L3.1, U4.3 (ST2)

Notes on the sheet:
RS485 Transceiver

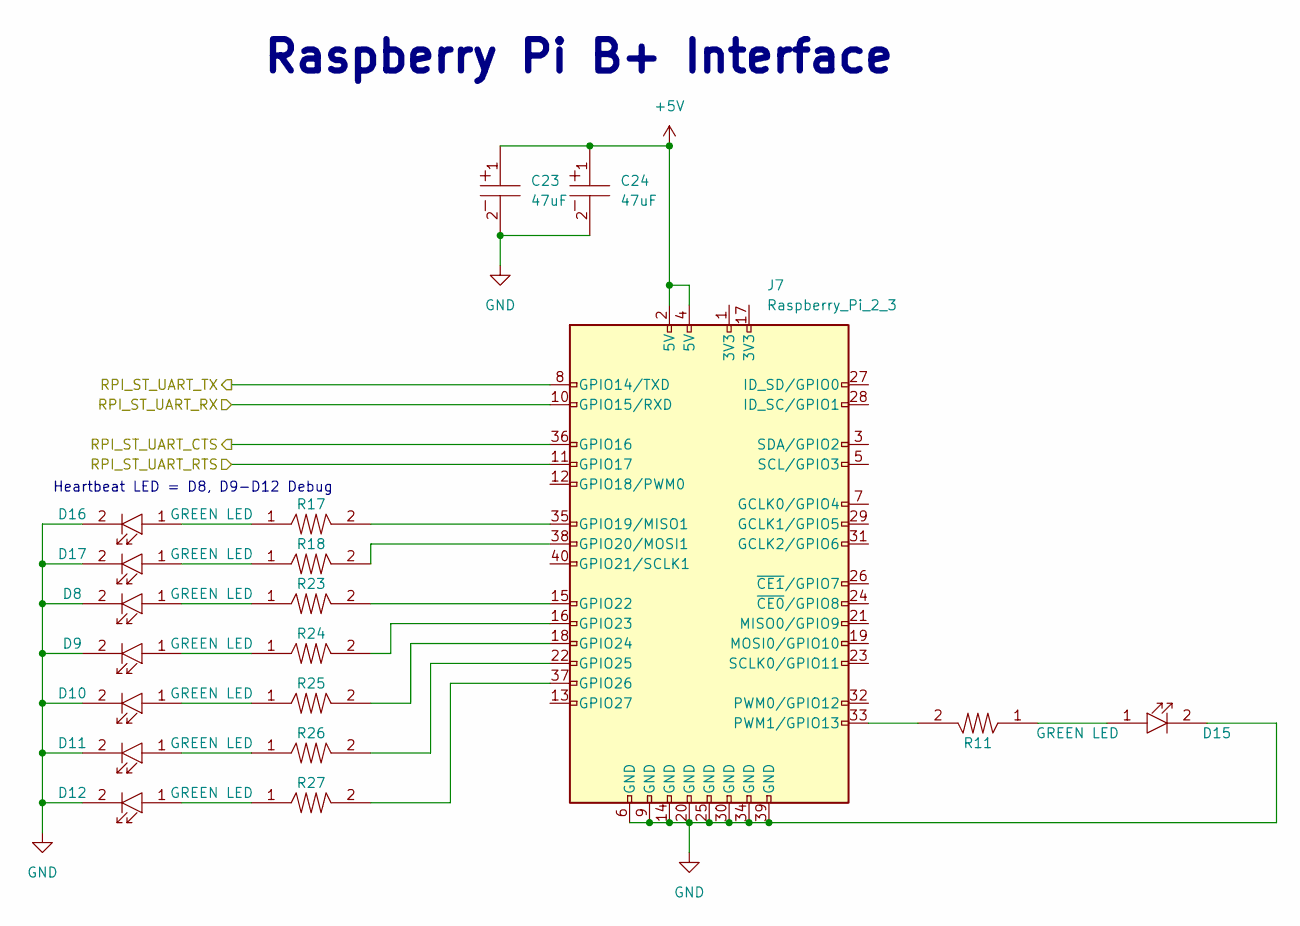
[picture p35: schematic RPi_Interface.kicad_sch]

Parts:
C23, C24: UCM1C470MCL1GS; Tolerance 20%; Voltage 16V; MFR# UCM1C470MCL1GS
D8, D9, D10, D11, D12, D15, D16, D17: LTST-C194KGKT; LED0603; Tolerance *; Voltage 2.1V; MFR# LTST-C194KGKT
J7: Raspberry_Pi_2_3; SULLINS_PPPC202LFBN-RC_RPi5
R11, R17, R18, R23, R24, R25, R26, R27: RC0603FR-07470RL; R0603; Tolerance 1%; Voltage *; MFR# RC0603FR-07470RL

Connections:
+5V: C23.1, C24.1, J7.2 (5V), J7.4 (5V); also elsewhere on the board
/RPi_Interface/RPI_ST_UART_CTS: J7.36 (GPIO16); also elsewhere on the board
/RPi_Interface/RPI_ST_UART_RTS: J7.11 (GPIO17); also elsewhere on the board
/RPi_Interface/RPI_ST_UART_RX: J7.10 (GPIO15/RXD); also elsewhere on the board
/RPi_Interface/RPI_ST_UART_TX: J7.8 (GPIO14/TXD); also elsewhere on the board
GND: C23.2, C24.2, D8.2, D9.2, D10.2, D11.2, D12.2, D15.2, D16.2, D17.2, J7.6 (GND), J7.9 (GND), J7.14 (GND), J7.20 (GND), J7.25 (GND), J7.30 (GND), J7.34 (GND), J7.39 (GND); also elsewhere on the board
unnamed: D8.1, R23.1
unnamed: D9.1, R24.1
unnamed: D10.1, R25.1
unnamed: D11.1, R26.1
unnamed: D12.1, R27.1
unnamed: D15.1, R11.1
unnamed: D16.1, R17.1
unnamed: D17.1, R18.1
unnamed: J7.35 (GPIO19/MISO1), R17.2
unnamed: J7.38 (GPIO20/MOSI1), R18.2
unnamed: J7.15 (GPIO22), R23.2
unnamed: J7.16 (GPIO23), R24.2
unnamed: J7.18 (GPIO24), R25.2
unnamed: J7.22 (GPIO25), R26.2
unnamed: J7.37 (GPIO26), R27.2
unnamed: J7.33 (PWM1/GPIO13), R11.2

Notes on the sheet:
Raspberry Pi B+ Interface
Heartbeat LED = D8, D9-D12 Debug

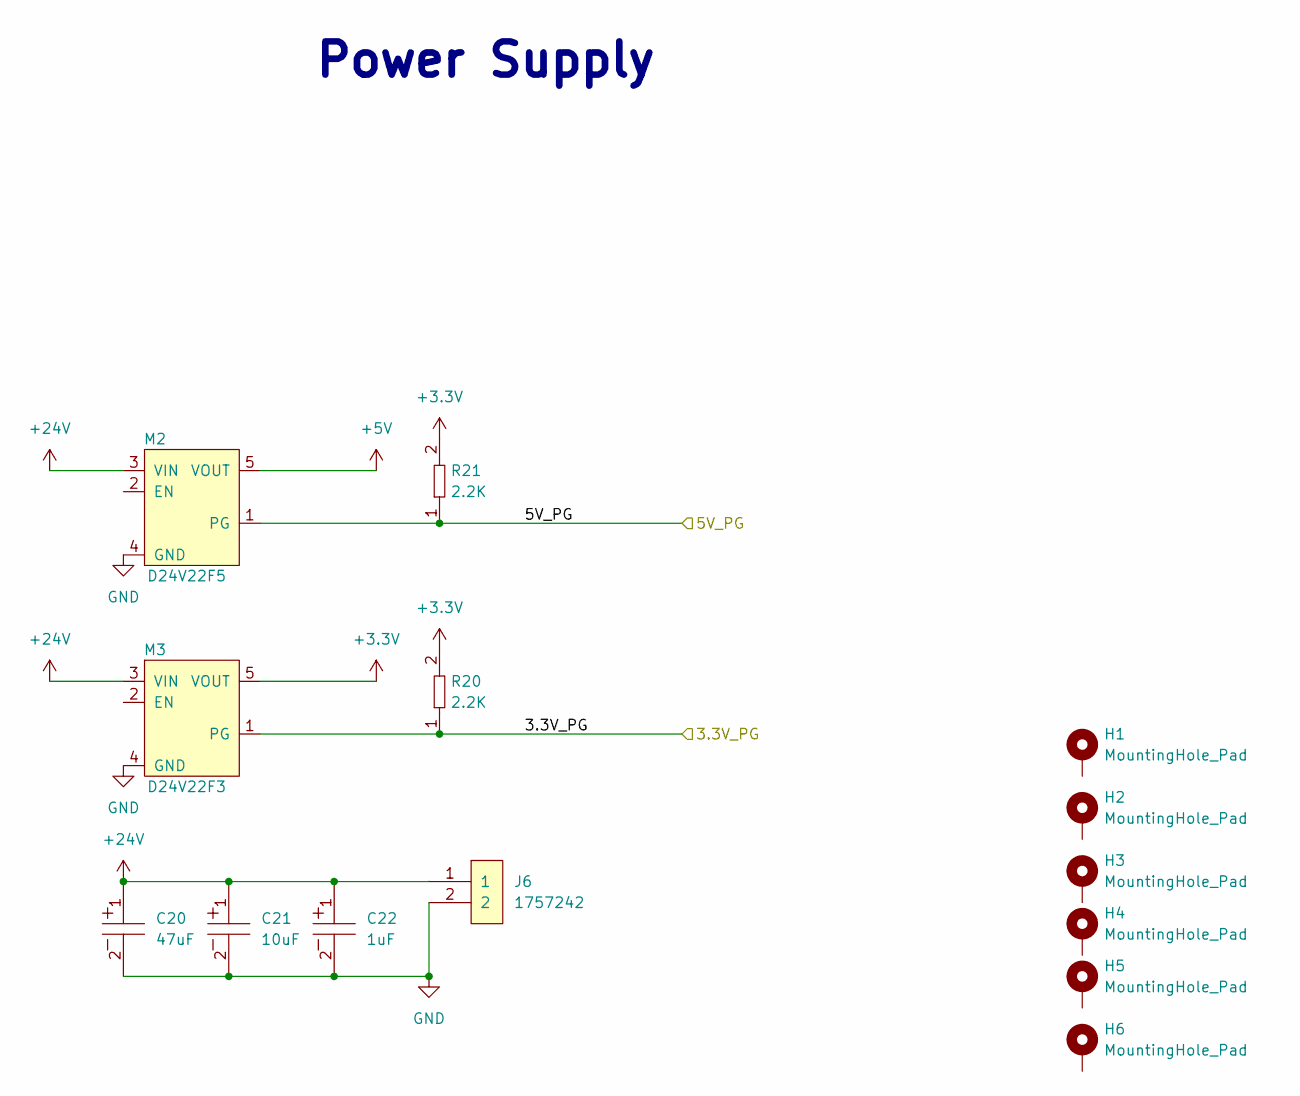
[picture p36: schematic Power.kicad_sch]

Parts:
C20: UUQ1H470MCL1GS; CP_Elec_8x10; Tolerance 20%; Voltage 50V; MFR# UUQ1H470MCL1GS
C21: UUQ1H100MCL1GB; CP_Elec_4x5.3; Tolerance 20%; Voltage 50V; MFR# UUQ1H100MCL1GB
C22: UUQ1H010MCL1GB; CP_Elec_4x5.3; Tolerance 20%; Voltage 50V; MFR# UUQ1H010MCL1GB
H1, H2, H3, H4, H5, H6: MountingHole_Pad; RPI_HAT_HOLE
J6: 1757242; PhoenixContact_MSTBA-G_02x5.08mm_Angled; Tolerance *; Voltage 300V; MFR# 1757242
M2: D24V22F5; D24V22F12; Tolerance N/A; Voltage 36V IN 5V OUT; MFR# D24V22F5
M3: D24V22F3; D24V22F12; Tolerance N/A; Voltage 36V IN 3.3V OUT; MFR# D24V22F3
R20, R21: RC0603FR-072K2L; R0603; Tolerance 1%; Voltage N/A; MFR# RC0603FR-072K2L

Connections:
+3.3V: M3.5 (VOUT), R20.2, R21.2; also elsewhere on the board
+5V: M2.5 (VOUT); also elsewhere on the board
+24V: C20.1, C21.1, C22.1, J6.1, M2.3 (VIN), M3.3 (VIN)
/Power/3.3V_PG: M3.1 (PG), R20.1; also elsewhere on the board
/Power/5V_PG: M2.1 (PG), R21.1; also elsewhere on the board
GND: C20.2, C21.2, C22.2, J6.2, M2.4 (GND), M3.4 (GND); also elsewhere on the board

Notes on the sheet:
Power Supply

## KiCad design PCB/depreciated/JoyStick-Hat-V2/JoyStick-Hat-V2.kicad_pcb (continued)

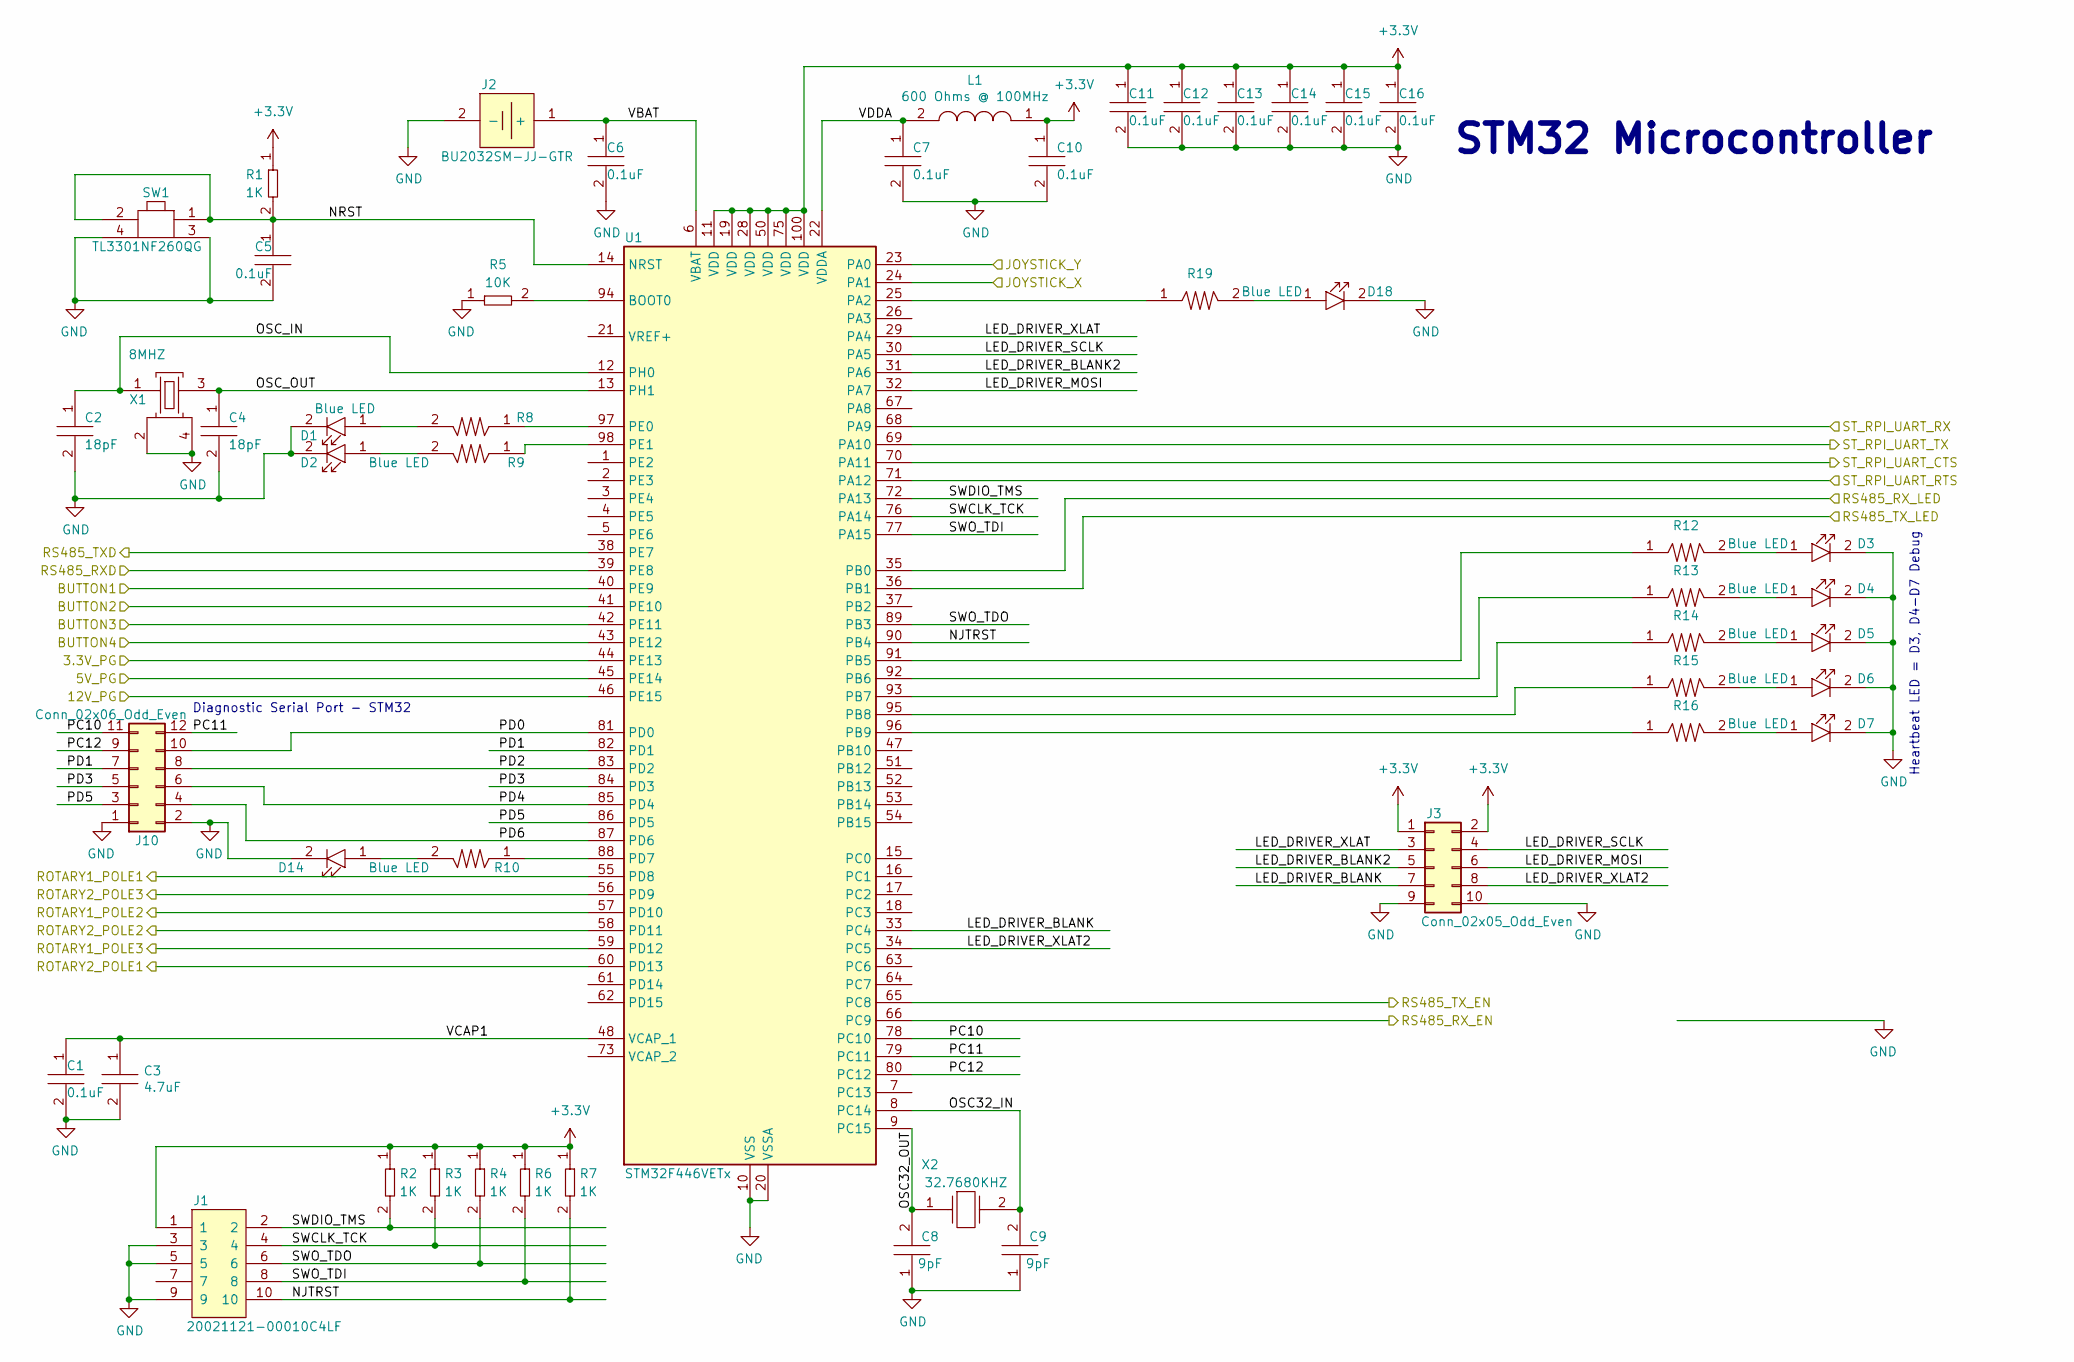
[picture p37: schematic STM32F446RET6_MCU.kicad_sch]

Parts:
C1, C5, C6, C7, C10, C11, C12, C13, C14, C15, C16: C0402C104K9PACTU; R0402; Tolerance 10%; Voltage 6.3V; MFR# C0402C104K9PACTU
C2, C4: GCM1555C1H180GA16D; C0402; Tolerance 2%; Voltage 50V; MFR# GCM1555C1H180GA16D
C3: GRM155R60J475ME47D; C0402; Tolerance 20%; Voltage 6.3V; MFR# GRM155R60J475ME47D
C8, C9: CL05C090CB5NNNC; C0402; Tolerance ±0.25pF; Voltage 50V; MFR# CL05C090CB5NNNC
D1, D2, D3, D4, D5, D6, D7, D14, D18: LTST-C194TBKT; LED0603; Tolerance *; Voltage 3.3V; MFR# LTST-C194TBKT
J1: 20021121-00010C4LF; Tolerance *; Voltage *; MFR# 20021121-00010C4LF
J2: BU2032SM-JJ-GTR; Tolerance *; Voltage 3.3V; MFR# BU2032SM-JJ-GTR
J3: Conn_02x05_Odd_Even; PinHeader_2x05_P2.54mm_Vertical
J10: Conn_02x06_Odd_Even; PinHeader_2x06_P2.54mm_Horizontal
L1: BLM15HG601SN1D; Tolerance *; Voltage *; MFR# BLM15HG601SN1D
R1, R2, R3, R4, R6, R7: RC0402FR-071KL; R0402; Tolerance 1%; Voltage *; MFR# RC0402FR-071KL
R5: RC0402FR-0710KL; R0402; Tolerance 1%; Voltage *; MFR# RC0402FR-0710KL
R8, R9, R10, R12, R13, R14, R15, R16, R19: RC0603FR-07470RL; R0603; Tolerance 1%; Voltage *; MFR# RC0603FR-07470RL
SW1: TL3301NF260QG; Tolerance *; Voltage 12VDC; MFR# TL3301NF260QG
U1: STM32F446VETx; LQFP-100_14x14mm_P0.5mm
X1: ABM3B-8.000MHZ-B2-T; ABM3B8.000MHZB2T; Tolerance *; Voltage *; MFR# ABM3B-8.000MHZ-B2-T
X2: ABS07-32.768KHZ-9-T; Tolerance *; Voltage *; MFR# ABS07-32.768KHZ-9-T

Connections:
+3.3V: C10.1, C11.1, C12.1, C13.1, C14.1, C15.1, C16.1, J1.1, J3.1, J3.2, L1.1, R1.1, R2.1, R3.1, R4.1, R6.1, R7.1, U1.11 (VDD), U1.19 (VDD), U1.28 (VDD), U1.50 (VDD), U1.75 (VDD), U1.100 (VDD); also elsewhere on the board
/JoyStick Interface/BUTTON1: U1.40 (PE9); also elsewhere on the board
/JoyStick Interface/BUTTON2: U1.41 (PE10); also elsewhere on the board
/JoyStick Interface/BUTTON3: U1.42 (PE11); also elsewhere on the board
/JoyStick Interface/BUTTON4: U1.43 (PE12); also elsewhere on the board
/JoyStick Interface/JOYSTICK_X: U1.24 (PA1); also elsewhere on the board
/JoyStick Interface/JOYSTICK_Y: U1.23 (PA0); also elsewhere on the board
/JoyStick Interface/ROTARY1_POLE1: U1.55 (PD8); also elsewhere on the board
/JoyStick Interface/ROTARY1_POLE2: U1.57 (PD10); also elsewhere on the board
/JoyStick Interface/ROTARY1_POLE3: U1.59 (PD12); also elsewhere on the board
/JoyStick Interface/ROTARY2_POLE1: U1.60 (PD13); also elsewhere on the board
/JoyStick Interface/ROTARY2_POLE2: U1.58 (PD11); also elsewhere on the board
/JoyStick Interface/ROTARY2_POLE3: U1.56 (PD9); also elsewhere on the board
/Power/3.3V_PG: U1.44 (PE13); also elsewhere on the board
/Power/5V_PG: U1.45 (PE14); also elsewhere on the board
/RPi_Interface/RPI_ST_UART_CTS: U1.71 (PA12); also elsewhere on the board
/RPi_Interface/RPI_ST_UART_RTS: U1.70 (PA11); also elsewhere on the board
/RPi_Interface/RPI_ST_UART_RX: U1.68 (PA9); also elsewhere on the board
/RPi_Interface/RPI_ST_UART_TX: U1.69 (PA10); also elsewhere on the board
/RS485 To Motor Controller Interface/RS485_RXD: U1.39 (PE8); also elsewhere on the board
/RS485 To Motor Controller Interface/RS485_RX_EN: U1.66 (PC9); also elsewhere on the board
/RS485 To Motor Controller Interface/RS485_RX_LED: U1.35 (PB0); also elsewhere on the board
/RS485 To Motor Controller Interface/RS485_TXD: U1.38 (PE7); also elsewhere on the board
/RS485 To Motor Controller Interface/RS485_TX_EN: U1.65 (PC8); also elsewhere on the board
/RS485 To Motor Controller Interface/RS485_TX_LED: U1.36 (PB1); also elsewhere on the board
/STM32F446RET6-MCU/12V_PG: U1.46 (PE15)
/STM32F446RET6-MCU/LED_DRIVER_BLANK: J3.7, U1.33 (PC4)
/STM32F446RET6-MCU/LED_DRIVER_BLANK2: J3.5, U1.31 (PA6)
/STM32F446RET6-MCU/LED_DRIVER_MOSI: J3.6, U1.32 (PA7)
/STM32F446RET6-MCU/LED_DRIVER_SCLK: J3.4, U1.30 (PA5)
/STM32F446RET6-MCU/LED_DRIVER_XLAT: J3.3, U1.29 (PA4)
/STM32F446RET6-MCU/LED_DRIVER_XLAT2: J3.8, U1.34 (PC5)
/STM32F446RET6-MCU/NJTRST: J1.10, R7.2, U1.90 (PB4)
/STM32F446RET6-MCU/NRST: C5.1, R1.2, SW1.1, SW1.2, U1.14 (NRST)
/STM32F446RET6-MCU/OSC32_IN: C9.2, U1.8 (PC14), X2.2
/STM32F446RET6-MCU/OSC32_OUT: C8.2, U1.9 (PC15), X2.1
/STM32F446RET6-MCU/OSC_IN: C2.1, U1.12 (PH0), X1.1
/STM32F446RET6-MCU/OSC_OUT: C4.1, U1.13 (PH1), X1.3
/STM32F446RET6-MCU/PC10: J10.11, U1.78 (PC10)
/STM32F446RET6-MCU/PC11: J10.12, U1.79 (PC11)
/STM32F446RET6-MCU/PC12: J10.9, U1.80 (PC12)
/STM32F446RET6-MCU/PD0: J10.10, U1.81 (PD0)
/STM32F446RET6-MCU/PD1: J10.7, U1.82 (PD1)
/STM32F446RET6-MCU/PD2: J10.8, U1.83 (PD2)
/STM32F446RET6-MCU/PD3: J10.5, U1.84 (PD3)
/STM32F446RET6-MCU/PD4: J10.6, U1.85 (PD4)
/STM32F446RET6-MCU/PD5: J10.3, U1.86 (PD5)
/STM32F446RET6-MCU/PD6: J10.4, U1.87 (PD6)
/STM32F446RET6-MCU/SWCLK_TCK: J1.4, R3.2, U1.76 (PA14)
/STM32F446RET6-MCU/SWDIO_TMS: J1.2, R2.2, U1.72 (PA13)
/STM32F446RET6-MCU/SWO_TDI: J1.8, R6.2, U1.77 (PA15)
/STM32F446RET6-MCU/SWO_TDO: J1.6, R4.2, U1.89 (PB3)
/STM32F446RET6-MCU/VBAT: C6.1, J2.1 (+), U1.6 (VBAT)
/STM32F446RET6-MCU/VCAP1: C1.1, C3.1, U1.48 (VCAP_1)
/STM32F446RET6-MCU/VDDA: C7.1, L1.2, U1.22 (VDDA)
GND: C1.2, C2.2, C3.2, C4.2, C5.2, C6.2, C7.2, C8.1, C9.1, C10.2, C11.2, C12.2, C13.2, C14.2, C15.2, C16.2, D1.2, D2.2, D3.2, D4.2, D5.2, D6.2, D7.2, D14.2, D18.2, J1.3, J1.5, J1.9, J2.2 (-), J3.9, J3.10, J10.1, J10.2, R5.1, SW1.3, SW1.4, U1.10 (VSS), U1.20 (VSSA), U1.27 (VSS), U1.49 (VSS), U1.74 (VSS), U1.99 (VSS), X1.2, X1.4; also elsewhere on the board
unnamed: D1.1, R8.2
unnamed: D2.1, R9.2
unnamed: D3.1, R12.2
unnamed: D4.1, R13.2
unnamed: D5.1, R14.2
unnamed: D6.1, R15.2
unnamed: D7.1, R16.2
unnamed: D14.1, R10.2
unnamed: D18.1, R19.2
unnamed: R5.2, U1.94 (BOOT0)
unnamed: R19.1, U1.25 (PA2)
unnamed: R12.1, U1.91 (PB5)
unnamed: R13.1, U1.92 (PB6)
unnamed: R14.1, U1.93 (PB7)
unnamed: R15.1, U1.95 (PB8)
unnamed: R16.1, U1.96 (PB9)
unnamed: R10.1, U1.88 (PD7)
unnamed: R8.1, U1.97 (PE0)
unnamed: R9.1, U1.98 (PE1)

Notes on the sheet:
Heartbeat LED = D3, D4-D7 Debug
STM32 Microcontroller
Diagnostic Serial Port - STM32

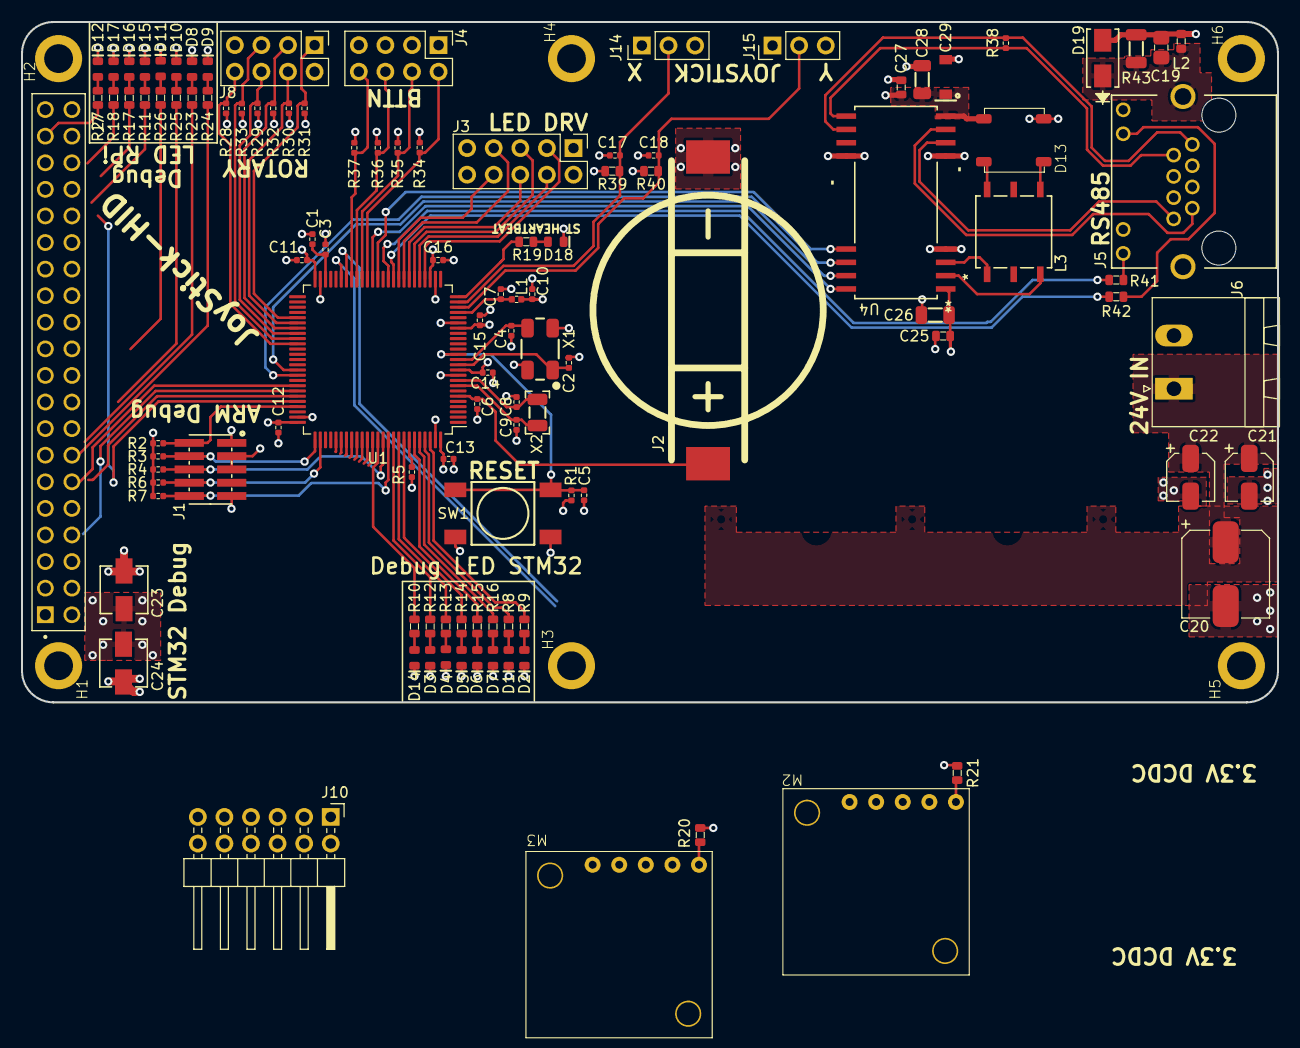
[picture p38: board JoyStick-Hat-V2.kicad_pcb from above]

Board: 4 copper layers, 120.0 x 65.0 mm, 117 parts (0 on the bottom side), 104 nets.

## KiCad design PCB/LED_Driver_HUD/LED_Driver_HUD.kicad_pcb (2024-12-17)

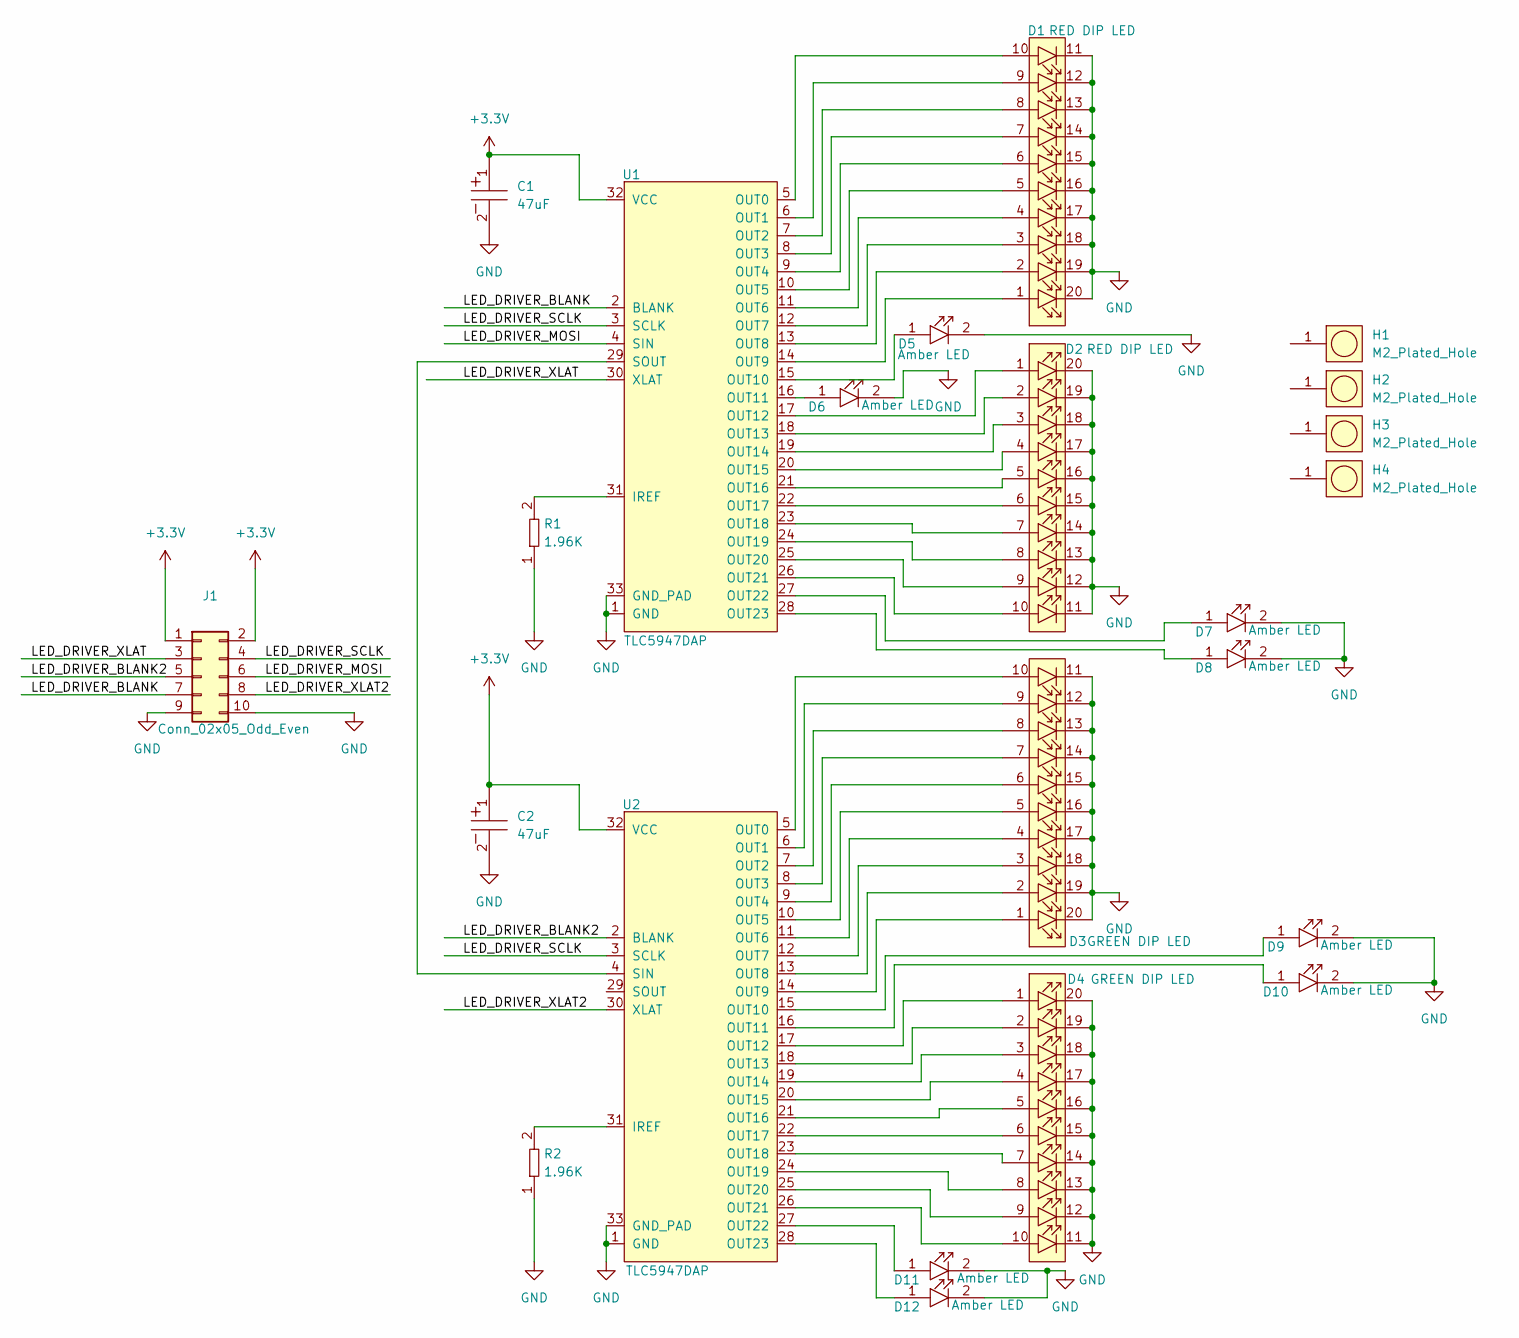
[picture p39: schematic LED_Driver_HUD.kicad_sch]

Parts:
C1, C2: UCM1C470MCL1GS; Tolerance 20%; Voltage 16V; MFR# UCM1C470MCL1GS
D1, D2: DC10EWA; DIP750W50P254L2540H825Q20; Tolerance *; Voltage 2V; MFR# DC10EWA
D3, D4: DC10GWA; DIP750W50P254L2540H825Q20; Tolerance *; Voltage 2.2V; MFR# DC10GWA
D5, D6, D7, D8, D9, D10, D11, D12: HLMP-1401; HLMP; Tolerance *; Voltage 2V; MFR# HLMP-1401
H1, H2, H3, H4: M2_Plated_Hole; M2_HOLE; Tolerance *; Voltage *; MFR# *
J1: Conn_02x05_Odd_Even; PinHeader_2x05_P2.54mm_Vertical
R1, R2: RC0805FR-071K96L; R0805; Tolerance 1%; Voltage N/A; MFR# RC0805FR-071K96L
U1, U2: TLC5947DAP; DAP32_4P36X4P11; Tolerance N/A; Voltage 3-5.5VDC; MFR# TLC5947DAP

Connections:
+3.3V: C1.1, C2.1, J1.1, J1.2, U1.32 (VCC), U2.32 (VCC)
/LED_DRIVER_BLANK: J1.7, U1.2 (BLANK)
/LED_DRIVER_BLANK2: J1.5, U2.2 (BLANK)
/LED_DRIVER_MOSI: J1.6, U1.4 (SIN)
/LED_DRIVER_SCLK: J1.4, U1.3 (SCLK), U2.3 (SCLK)
/LED_DRIVER_XLAT: J1.3, U1.30 (XLAT)
/LED_DRIVER_XLAT2: J1.8, U2.30 (XLAT)
GND: C1.2, C2.2, D1.11, D1.12, D1.13, D1.14, D1.15, D1.16, D1.17, D1.18, D1.19, D1.20, D2.11, D2.12, D2.13, D2.14, D2.15, D2.16, D2.17, D2.18, D2.19, D2.20, D3.11, D3.12, D3.13, D3.14, D3.15, D3.16, D3.17, D3.18, D3.19, D3.20, D4.11, D4.12, D4.13, D4.14, D4.15, D4.16, D4.17, D4.18, D4.19, D4.20, D5.2, D6.2, D7.2, D8.2, D9.2, D10.2, D11.2, D12.2, J1.9, J1.10, R1.1, R2.1, U1.1 (GND), U1.33 (GND_PAD), U2.1 (GND), U2.33 (GND_PAD)
unnamed: R1.2, U1.31 (IREF)
unnamed: D1.10, U1.5 (OUT0)
unnamed: D1.9, U1.6 (OUT1)
unnamed: D1.8, U1.7 (OUT2)
unnamed: D1.7, U1.8 (OUT3)
unnamed: D1.6, U1.9 (OUT4)
unnamed: D1.5, U1.10 (OUT5)
unnamed: D1.4, U1.11 (OUT6)
unnamed: D1.3, U1.12 (OUT7)
unnamed: D1.2, U1.13 (OUT8)
unnamed: D1.1, U1.14 (OUT9)
unnamed: D5.1, U1.15 (OUT10)
unnamed: D6.1, U1.16 (OUT11)
unnamed: D2.1, U1.17 (OUT12)
unnamed: D2.2, U1.18 (OUT13)
unnamed: D2.3, U1.19 (OUT14)
unnamed: D2.4, U1.20 (OUT15)
unnamed: D2.5, U1.21 (OUT16)
unnamed: D2.6, U1.22 (OUT17)
unnamed: D2.7, U1.23 (OUT18)
unnamed: D2.8, U1.24 (OUT19)
unnamed: D2.9, U1.25 (OUT20)
unnamed: D2.10, U1.26 (OUT21)
unnamed: D7.1, U1.27 (OUT22)
unnamed: D8.1, U1.28 (OUT23)
unnamed: U1.29 (SOUT), U2.4 (SIN)
unnamed: R2.2, U2.31 (IREF)
unnamed: D3.10, U2.5 (OUT0)
unnamed: D3.9, U2.6 (OUT1)
unnamed: D3.8, U2.7 (OUT2)
unnamed: D3.7, U2.8 (OUT3)
unnamed: D3.6, U2.9 (OUT4)
unnamed: D3.5, U2.10 (OUT5)
unnamed: D3.4, U2.11 (OUT6)
unnamed: D3.3, U2.12 (OUT7)
unnamed: D3.2, U2.13 (OUT8)
unnamed: D3.1, U2.14 (OUT9)
unnamed: D9.1, U2.15 (OUT10)
unnamed: D10.1, U2.16 (OUT11)
unnamed: D4.1, U2.17 (OUT12)
unnamed: D4.2, U2.18 (OUT13)
unnamed: D4.3, U2.19 (OUT14)
unnamed: D4.4, U2.20 (OUT15)
unnamed: D4.5, U2.21 (OUT16)
unnamed: D4.6, U2.22 (OUT17)
unnamed: D4.7, U2.23 (OUT18)
unnamed: D4.8, U2.24 (OUT19)
unnamed: D4.9, U2.25 (OUT20)
unnamed: D4.10, U2.26 (OUT21)
unnamed: D11.1, U2.27 (OUT22)
unnamed: D12.1, U2.28 (OUT23)

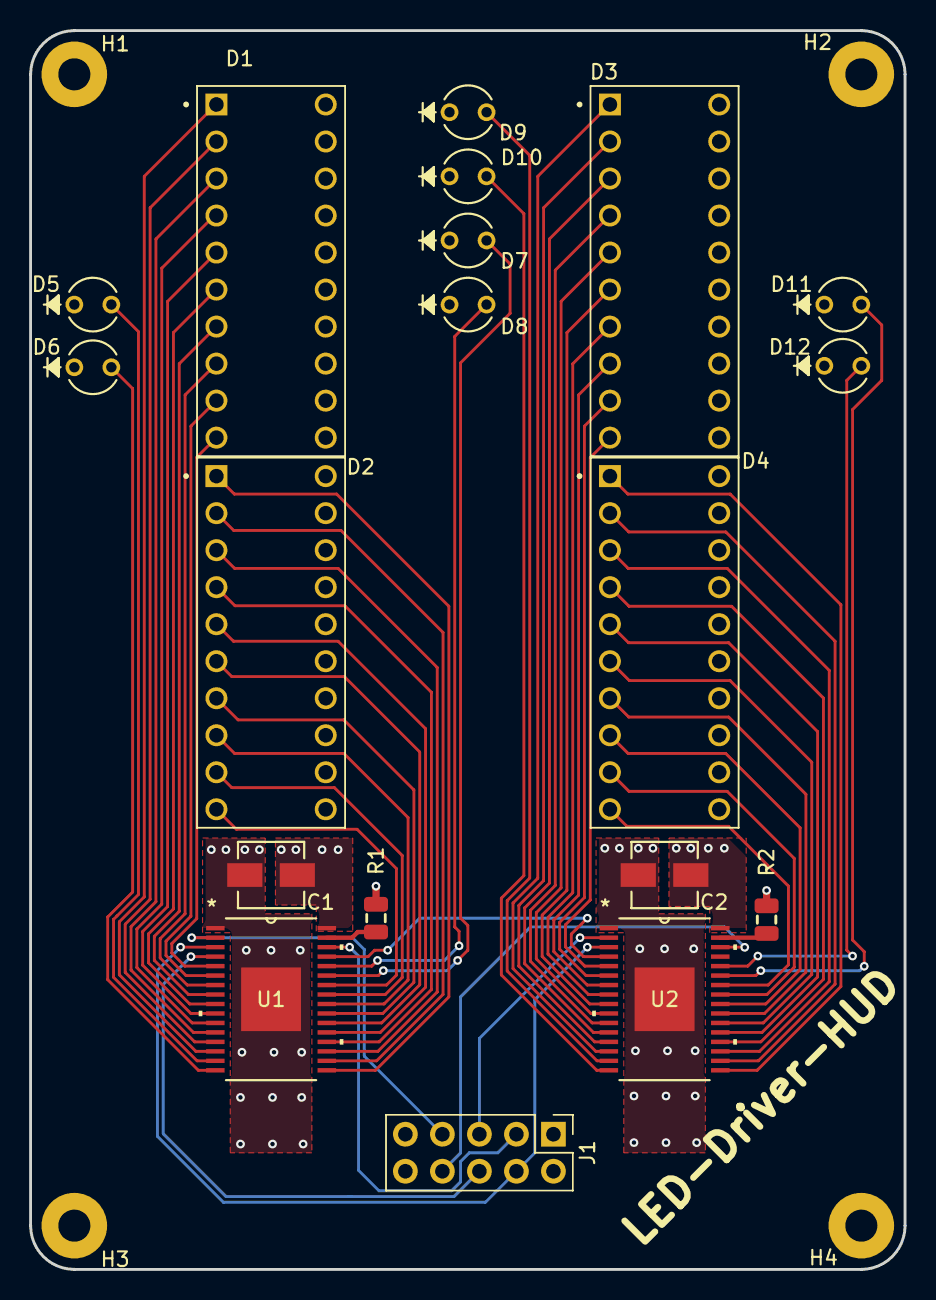
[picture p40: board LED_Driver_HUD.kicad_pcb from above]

Board: 4 copper layers, 60.0 x 85.0 mm, 23 parts (0 on the bottom side), 59 nets.

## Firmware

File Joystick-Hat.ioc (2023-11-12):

#MicroXplorer Configuration settings - do not modify
ADC1.Channel-1\#ChannelRegularConversion=ADC_CHANNEL_0
ADC1.IPParameters=Rank-1\#ChannelRegularConversion,master,Channel-1\#ChannelRegularConversion,SamplingTime-1\#ChannelRegularConversion,NbrOfConversionFlag
ADC1.NbrOfConversionFlag=1
ADC1.Rank-1\#ChannelRegularConversion=1
ADC1.SamplingTime-1\#ChannelRegularConversion=ADC_SAMPLETIME_3CYCLES
ADC1.master=1
CAD.formats=
CAD.pinconfig=
CAD.provider=
File.Version=6
GPIO.groupedBy=
KeepUserPlacement=false
Mcu.CPN=STM32F446VET6
Mcu.Family=STM32F4
Mcu.IP0=ADC1
Mcu.IP1=NVIC
Mcu.IP2=RCC
Mcu.IP3=SPI1
Mcu.IP4=SYS
Mcu.IP5=UART5
Mcu.IP6=USART1
Mcu.IP7=USART2
Mcu.IPNb=8
Mcu.Name=STM32F446V(C-E)Tx
Mcu.Package=LQFP100
Mcu.Pin0=PA0-WKUP
Mcu.Pin1=PA1
Mcu.Pin10=PC8
Mcu.Pin11=PC9
Mcu.Pin12=PA9
Mcu.Pin13=PA10
Mcu.Pin14=PA11
Mcu.Pin15=PA12
Mcu.Pin16=PD3
Mcu.Pin17=PD4
Mcu.Pin18=PD5
Mcu.Pin19=PD6
Mcu.Pin2=PA2
Mcu.Pin20=VP_SYS_VS_Systick
Mcu.Pin3=PA3
Mcu.Pin4=PA4
Mcu.Pin5=PA5
Mcu.Pin6=PA6
Mcu.Pin7=PA7
Mcu.Pin8=PE7
Mcu.Pin9=PE8
Mcu.PinsNb=21
Mcu.ThirdPartyNb=0
Mcu.UserConstants=
Mcu.UserName=STM32F446VETx
MxCube.Version=6.9.2
MxDb.Version=DB.6.0.92
NVIC.BusFault_IRQn=true\:0\:0\:false\:false\:true\:false\:false\:false
NVIC.DebugMonitor_IRQn=true\:0\:0\:false\:false\:true\:false\:false\:false
NVIC.ForceEnableDMAVector=true
NVIC.HardFault_IRQn=true\:0\:0\:false\:false\:true\:false\:false\:false
NVIC.MemoryManagement_IRQn=true\:0\:0\:false\:false\:true\:false\:false\:false
NVIC.NonMaskableInt_IRQn=true\:0\:0\:false\:false\:true\:false\:false\:false
NVIC.PendSV_IRQn=true\:0\:0\:false\:false\:true\:false\:false\:false
NVIC.PriorityGroup=NVIC_PRIORITYGROUP_4
NVIC.SVCall_IRQn=true\:0\:0\:false\:false\:true\:false\:false\:false
NVIC.SysTick_IRQn=true\:15\:0\:false\:false\:true\:false\:true\:false
NVIC.UsageFault_IRQn=true\:0\:0\:false\:false\:true\:false\:false\:false
PA0-WKUP.Signal=ADCx_IN0
PA1.Signal=ADCx_IN1
PA10.Mode=Asynchronous
PA10.Signal=USART1_RX
PA11.Mode=CTS_RTS
PA11.Signal=USART1_CTS
PA12.Mode=CTS_RTS
PA12.Signal=USART1_RTS
PA2.Signal=ADCx_IN2
PA3.Signal=ADCx_IN3
PA4.Signal=ADCx_IN4
PA5.Mode=Full_Duplex_Master
PA5.Signal=SPI1_SCK
PA6.Mode=Full_Duplex_Master
PA6.Signal=SPI1_MISO
PA7.Mode=Full_Duplex_Master
PA7.Signal=SPI1_MOSI
PA9.Mode=Asynchronous
PA9.Signal=USART1_TX
PC8.Mode=CTS_RTS
PC8.Signal=UART5_RTS
PC9.Mode=CTS_RTS
PC9.Signal=UART5_CTS
PD3.Mode=CTS_RTS
PD3.Signal=USART2_CTS
PD4.Mode=CTS_RTS
PD4.Signal=USART2_RTS
PD5.Mode=Asynchronous
PD5.Signal=USART2_TX
PD6.Mode=Asynchronous
PD6.Signal=USART2_RX
PE7.Mode=Asynchronous
PE7.Signal=UART5_RX
PE8.Mode=Asynchronous
PE8.Signal=UART5_TX
PinOutPanel.RotationAngle=0
ProjectManager.AskForMigrate=true
ProjectManager.BackupPrevious=false
ProjectManager.CompilerOptimize=6
ProjectManager.ComputerToolchain=false
ProjectManager.CoupleFile=false
ProjectManager.CustomerFirmwarePackage=
ProjectManager.DefaultFWLocation=true
ProjectManager.DeletePrevious=true
ProjectManager.DeviceId=STM32F446VETx
ProjectManager.FirmwarePackage=STM32Cube FW_F4 V1.27.1
ProjectManager.FreePins=false
ProjectManager.HalAssertFull=false
ProjectManager.HeapSize=0x200
ProjectManager.KeepUserCode=true
ProjectManager.LastFirmware=true
ProjectManager.LibraryCopy=0
ProjectManager.MainLocation=Core/Src
ProjectManager.NoMain=false
ProjectManager.PreviousToolchain=
ProjectManager.ProjectBuild=false
ProjectManager.ProjectFileName=Joystick-Hat.ioc
ProjectManager.ProjectName=Joystick-Hat
ProjectManager.ProjectStructure=
ProjectManager.RegisterCallBack=
ProjectManager.StackSize=0x400
ProjectManager.TargetToolchain=EWARM V8.50
ProjectManager.ToolChainLocation=
ProjectManager.UAScriptAfterPath=
ProjectManager.UAScriptBeforePath=
ProjectManager.UnderRoot=false
ProjectManager.functionlistsort=1-SystemClock_Config-RCC-false-HAL-false,2-MX_GPIO_Init-GPIO-false-HAL-true,3-MX_ADC1_Init-ADC1-false-HAL-true,4-MX_SPI1_Init-SPI1-false-HAL-true,5-MX_UART5_Init-UART5-false-HAL-true,6-MX_USART1_UART_Init-USART1-false-HAL-true
RCC.CECFreq_Value=32786.88524590164
RCC.CortexFreq_Value=16000000
RCC.FamilyName=M
RCC.IPParameters=CECFreq_Value,CortexFreq_Value,FamilyName,PLLCLKFreq_Value,PLLI2SPCLKFreq_Value,PLLI2SQCLKFreq_Value,PLLI2SRCLKFreq_Value,PLLQCLKFreq_Value,PLLRCLKFreq_Value,PLLSAIPCLKFreq_Value,PLLSAIQCLKFreq_Value,SAIAFreq_Value,SAIBFreq_Value,SDIOFreq_Value,USBFreq_Value,VCOI2SInputFreq_Value,VCOI2SOutputFreq_Value,VCOInputFreq_Value,VCOOutputFreq_Value,VCOSAIInputFreq_Value,VCOSAIOutputFreq_Value
RCC.PLLCLKFreq_Value=96000000
RCC.PLLI2SPCLKFreq_Value=96000000
RCC.PLLI2SQCLKFreq_Value=96000000
RCC.PLLI2SRCLKFreq_Value=96000000
RCC.PLLQCLKFreq_Value=96000000
RCC.PLLRCLKFreq_Value=96000000
RCC.PLLSAIPCLKFreq_Value=96000000
RCC.PLLSAIQCLKFreq_Value=96000000
RCC.SAIAFreq_Value=96000000
RCC.SAIBFreq_Value=96000000
RCC.SDIOFreq_Value=96000000
RCC.USBFreq_Value=96000000
RCC.VCOI2SInputFreq_Value=1000000
RCC.VCOI2SOutputFreq_Value=192000000
RCC.VCOInputFreq_Value=1000000
RCC.VCOOutputFreq_Value=192000000
RCC.VCOSAIInputFreq_Value=1000000
RCC.VCOSAIOutputFreq_Value=192000000
SH.ADCx_IN0.0=ADC1_IN0,IN0
SH.ADCx_IN0.ConfNb=1
SH.ADCx_IN1.0=ADC1_IN1,IN1
SH.ADCx_IN1.ConfNb=1
SH.ADCx_IN2.0=ADC1_IN2,IN2
SH.ADCx_IN2.ConfNb=1
SH.ADCx_IN3.0=ADC1_IN3,IN3
SH.ADCx_IN3.ConfNb=1
SH.ADCx_IN4.0=ADC1_IN4,IN4
SH.ADCx_IN4.ConfNb=1
SPI1.CalculateBaudRate=8.0 MBits/s
SPI1.Direction=SPI_DIRECTION_2LINES
SPI1.IPParameters=VirtualType,Mode,Direction,CalculateBaudRate
SPI1.Mode=SPI_MODE_MASTER
SPI1.VirtualType=VM_MASTER
UART5.IPParameters=VirtualMode
UART5.VirtualMode=Asynchronous
USART1.IPParameters=VirtualMode
USART1.VirtualMode=VM_ASYNC
USART2.IPParameters=VirtualMode
USART2.VirtualMode=VM_ASYNC
VP_SYS_VS_Systick.Mode=SysTick
VP_SYS_VS_Systick.Signal=SYS_VS_Systick
board=custom

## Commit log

2023-08-24 Schematic and Libraries
    Started the schematic and started making footprints and symbols for the new components needed in the design.
    [JoyStick-Hat.kicad_pcb, JoyStick-Hat.kicad_sch, LED_Driver_Power.kicad_sch, LED_Driver_Speed.kicad_sch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]
2023-09-22 MCU
    MCU schematic added and 90% complete
    [STM32F446RET6_MCU.kicad_sch]
2023-09-27 Power and LED Driver
    Power Supply Schematic sketched out using Pololu power regulator modules to hasten design. LED drivers replaced with ones that have 24 ouputs so we can use 20 unit bar graph LEDs and have 8 extra cha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
    [JoyStick-Hat.kicad_sch, JoyStick.kicad_sch, LED_Driver_Power.kicad_sch, LED_Driver_Speed.kicad_sch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]
2023-10-04 LED drivers and Joystick
    Finished LED driver scheamtics, corrected some problems with symbols. added conenctors for joystick and buttons, connected RPI pins to MCU
    [JoyStick-Hat.kicad_sch, JoyStick.kicad_sch, LED_Driver_Power.kicad_sch, LED_Driver_Speed.kicad_sch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]
2023-10-04 Sheet Conenctivity and RS485
    Added more sheet entries throughuot the project connecting different subsystems to the main MCU schematic. Also added new sheet for the RS485 interface for communicating with the motor control board.
    [JoyStick-Hat.kicad_sch, JoyStick.kicad_sch, Power.kicad_sch, RS485_TO_MOTOR.kicad_sch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]
2023-10-20 Schematic Progress
    Made progress with schematic and corrected designator letters with connectors to match the built in paradigm of using J instead of T. T will not be used to referencing transformers instead of connect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
    [JoyStick-Hat.kicad_sch, JoyStick.kicad_sch, LED_Driver_Power.kicad_sch, LED_Driver_Speed.kicad_sch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]
2023-11-12 Schematic Complete
    Schematic completed. Moved to 100 pin version of STM32 MCU for more connectivity and better muxing of internal peripherals with pins.
    [JoyStick-Hat.kicad_sch, LED_Driver_Power.kicad_sch, LED_Driver_Speed.kicad_sch, RPi_Interface.kicad_sch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]
2023-11-12 PCB Created
    Schematic and footprint bugs knocked out PCB created and parts imported into board.
    [JoyStick-Hat.kicad_pcb, JoyStick.kicad_sch, RPi_Interface.kicad_sch, STM32F446RET6_MCU.kicad_sch]
2023-11-12 LEDs and Additional connectors
    Added heartbeat and diagnostic LEDs to STM32 and RPi3 schematics so we can directly flash them for debug purposes. Added a connector for serial port diagnostics on STM32. Added rotary switch interfac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
    [JoyStick-Hat.kicad_pcb, JoyStick-Hat.kicad_sch, JoyStick.kicad_sch, LED_Driver_Power.kicad_sch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]
2023-11-18 Board Shape and Layout
    Board Shape added and layout started !
    [JoyStick-Hat.kicad_pcb, JoyStick.kicad_sch, Joystick_Hat_Board_shape.dxf]
2023-11-21 Design Rules, Component Placement. Features Dropped
    Added design rules for OSHPark.com to PCB, Most components placed roughly for whole board more to follow and more tweaks,. Features were dropped/rearanged. USB for STM32 dropped as its not necessary.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
    [JoyStick-Hat.kicad_pcb, JoyStick-Hat.kicad_sch, JoyStick_Board_Shape_NoNotch120mm.dxf, Joy_Stick_Hat_Board_Shape_NoNotch.dxf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]
2023-12-12 Board Tweaks and progress
    Made progress with baord. Adjusted the position of RPi header to be correct and absolute. Changed location of regulator modules and power input capacitors. Added 3D models missing from the larger com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
    [JoyStick-Hat.kicad_pcb, JoyStick.kicad_sch, RPi_Interface.kicad_sch, RS485_TO_MOTOR.kicad_sch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]
2023-12-21 Board Routing
    Connectors swapped around and board route started
    [JoyStick-Hat.kicad_pcb, JoyStick.kicad_sch, Power.kicad_sch, RS485_TO_MOTOR.kicad_sch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]
2024-01-10 Board Progress
    Board route nearly complete, internal power plane topologys witched up to run 5Vs as plane. Reset buttom moved. Next: add more LEDs and breakout more STM32 pins for development purposes.
    [JoyStick-Hat.kicad_pcb, STM32F446RET6_MCU.kicad_sch]
2024-01-11 PCB First Pass Complete
    First complete pass at PCB finished. Added more debug LEDs for both STM32 and RPi, 8 totaly so binary data can be outputted as a byte etc, that way we can have debug codes. Added heartbeat LED to STM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
    [JoyStick-Hat.kicad_pcb, RPi_Interface.kicad_sch, STM32F446RET6_MCU.kicad_sch]
2024-01-23 BOM
    BOM Exported and converted to LibreOffice format
    [JoyStick-Hat.csv, JoyStick-Hat_BOM.ods]
2024-03-12 James Fixes and 3D models
    Added all the changes that James suggested to the design and then added 3D models to the board for mechanical design purposes. Generated 3D renders of the board and added them to new directory called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
    [JoyStick-Hat-B_Cu.gbl, JoyStick-Hat-B_Mask.gbs, JoyStick-Hat-B_Paste.gbp, JoyStick-Hat-B_Silkscreen.gbo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]
2024-03-12 LED_Driver_HUD and 2D render
    Added new project for LED Driver HUD board, a daughter board that drives LEDs for displaying battery power level and wheel chair set speed. Added 2D render of Joystick-HID Hat
    [LED_Driver_HUD.kicad_pcb, LED_Driver_HUD.kicad_sch]
2024-04-27 RJ45
    Replaced RJ45 connector, original one had magnetics, those are not needed for RS485 and would have caused problems. Hooked up coms LEDs on RJ45 connector to MCU for debugging and displaying coms acti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
    [JoyStick-Hat-B_Cu.gbl, JoyStick-Hat-B_Mask.gbs, JoyStick-Hat-B_Paste.gbp, JoyStick-Hat-B_Silkscreen.gbo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]
2024-04-27 Power Input Moved
    Power input connector moved to be flush with board!
    [JoyStick-Hat.kicad_pcb]
2024-05-21 Board Tweaks
    Copper pour specifications adjusted and repoured. DRC errors are caused by silkscreen , this happened when updating from KiCAD 7 to 8, still investigating it.
    [JoyStick-Hat.csv, JoyStick-Hat.kicad_pcb, JoyStick-Hat.kicad_sch, JoyStick-Hat.ods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]
2024-05-23 BOM
    Bom saved in libreoffice format
    [JoyStick-Hat.ods]
2024-07-08 Silkscreen Tweaks
    Added lots of labels to silkscreen and moved some traces
    [JoyStick-Hat.kicad_pcb]
2024-07-09 Connectors Moved, Labels Added, and New Images
    Moved connectors around so labels can be fit on the bottom of PCB, labels added to bottom of PCB. New images exported !
    [JoyStick-Hat.kicad_pcb, Power.kicad_sch]
2024-07-11 LED Driver HUD
    Finished PCB design of LED Driver HUD PCB, First pass of route DRC full pass. Next update adding additional LEDs for additional display functions
    [LED_Board_Shape.dxf, LED_Driver_HUD.kicad_pcb, LED_Driver_HUD.kicad_sch]
2024-07-11 LED HUD Complete
    Added Additional indicator LEDs to LED HUD board. Full DRC pass.
    [LED_Driver_HUD.kicad_pcb, LED_Driver_HUD.kicad_sch]
2024-07-23 Board ordered
    Board ordered
    [JoyStick-Hat.kicad_pcb]
2024-08-12 V2
    Started version 2 design and reworking
    [JoyStick-Hat-V2-Re-Imagined.csv, JoyStick-Hat-V2-Re-Imagined.kicad_pcb, JoyStick-Hat-V2-Re-Imagined.kicad_sch, JoyStick-Hat-V2.csv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]
2024-08-12 Assembly notes
    Started notes on assembly
    [JoyStick-Hat_BOM.ods, JoyStick-Hat_BOM_Assembly.ods, RS485_TO_MOTOR.kicad_sch]
2024-08-12 Joystick Hat V2 Progress
    Powersupply section laid out on V2 of JoyStick Hat PCB
    [JoyStick-Hat-V2-Re-Imagined.kicad_pcb, JoyStick-Hat-V2-Re-Imagined.kicad_sch, Power.kicad_sch]
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2024-08-22 V2
    Lots of progress made on version two of JoyStick Hat but the RPi 5 is going to be elimintated and an additional RS485 port added.
    [JoyStick-Hat-V2-Re-Imagined.kicad_pcb, JoyStick.kicad_sch, RPi_Interface.kicad_sch, STM32F446RET6_MCU.kicad_sch]
2024-09-04 RPi Removed
    Removed RPi from circuit added 20 pin JTAG schematic and PCB stil WIP
    [JoyStick-Hat-V2-Re-Imagined.kicad_pcb, JoyStick-Hat-V2-Re-Imagined.kicad_sch, STM32F446RET6_MCU.kicad_sch]
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2024-09-25 V2
    V2 Schematic and Debug connector on PCB corrected
    [JoyStick-Hat-V2-Re-Imagined.kicad_pcb]
2024-09-30 V2 PCB First PAss Complete
    First pass of V2 PCB Completeded !
    [JoyStick-Hat-V2-Re-Imagined.kicad_pcb]
2024-09-30 Schematic Tweak
    Making MCU page more readable
    [STM32F446RET6_MCU.kicad_sch]
2024-11-02 V2 Tweaks
    More Tweaks to the completed V2 design. 3D renders of V2 design produced and added to img folder for documentation update coming in the next commit. Photos of prototype also added to img folder for d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
    [JoyStick-Hat-V2-Re-Imagined.kicad_pcb, Power.kicad_sch]
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2024-12-17 Fab Fixes
    Fixing for Frabrication, DRC cleared by pending external review subject to change.
    [JoyStick-Hat-V2-Re-Imagined.kicad_pcb, JoyStick-Hat-V2-Re-Imagined.kicad_sch, LED_Driver_HUD.kicad_pcb, RS485_TO_MOTOR.kicad_sch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]
2024-12-18 STM32 Exp
    Removed 5V regulator, corrected RS485 schematic, added more expansion to STM32 since we had space.
    [JoyStick-Hat-V2-Re-Imagined.kicad_pcb, Power.kicad_sch, STM32F446RET6_MCU.kicad_sch]
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2024-12-20 RS485 Circuit Fixes, STM32 Expansion
    Fixe RS485 circuit errors, changed PCB topology for RS485. Added STM32 expansion IO in place of 5V Regulator.
    [JoyStick-Hat-V2-Re-Imagined.kicad_pcb, RS485_TO_MOTOR.kicad_sch, STM32F446RET6_MCU.kicad_sch]
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

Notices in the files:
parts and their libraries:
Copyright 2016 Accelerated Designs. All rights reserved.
